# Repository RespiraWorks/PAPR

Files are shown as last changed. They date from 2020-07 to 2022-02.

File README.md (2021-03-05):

# RespiraWorks PAPR Project

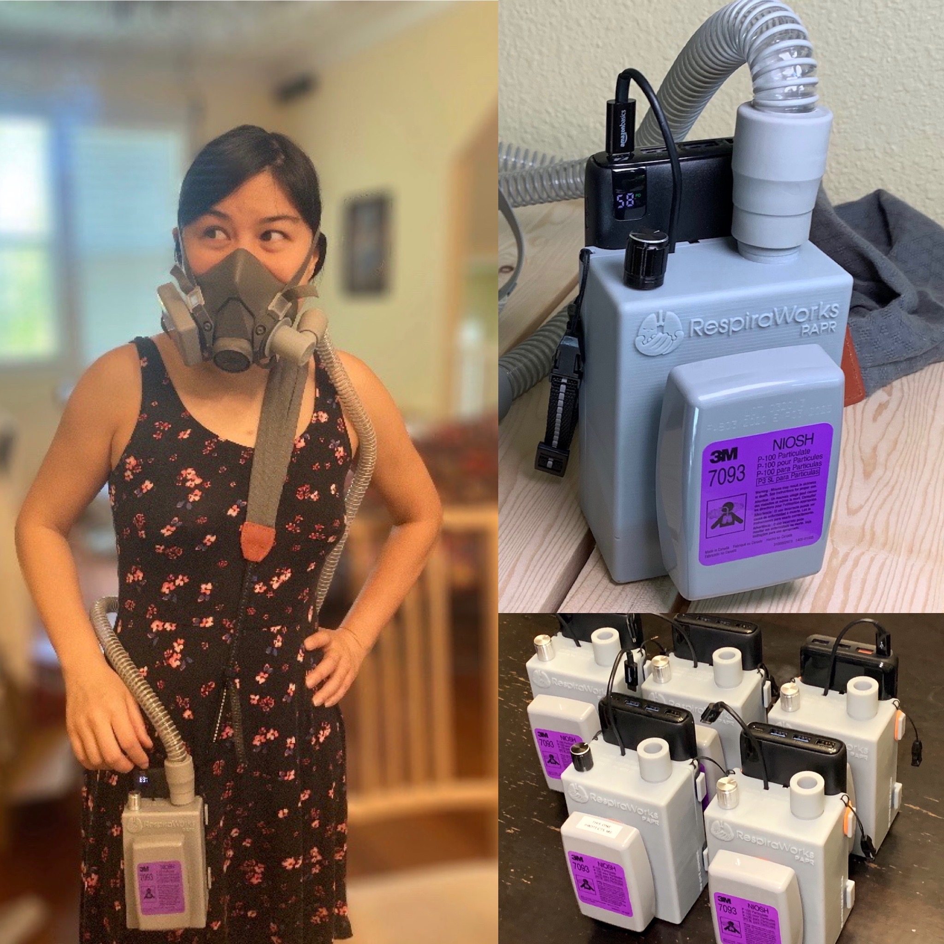
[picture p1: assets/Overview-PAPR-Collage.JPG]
Overview photo


***Important Disclaimer: This is a prototype device, offered free-of-charge as a public service during the COVID emergency, and no claim, guarantee, or warranty of performance or suitablity for any purpose is offered or implied.  This device has not been independently certified or approved.  Use of this design or any derivatives thereof is entirely at your own risk.  By using any of these materials, you acknowledge that you have read and understood the [full disclaimer](#full-disclaimer) at the end of this document.  Please do not use these materials if you do not understand and accept these risks.***

This is a low-cost 3D-printable PAPR project started by Edwin Chiu as part of RespiraWorks (github: inceptionev)

This project is currently at release-candidate stage.  The current files can be found in the release-candidates folder.  Most of the 3D files here were created in FreeCad v0.18.

The most current instructions are those in this README.  They include instructions both for building the PAPR and for modifying off-the-shelf masks, hoods, and helmets for use with the PAPR.

I am making this for myself, and for my loved ones who are medical workers and essential workers.  They wear masks all day to keep us safe, and supplies of disposable PPE are sometimes uncertain.

The combination of a respirator mask, powered air delivery, and commonly-available bayonet-mount filter packs provides a better face-seal, more comfortable breathing, and more re-usability than disposable masks. 

## Features:
- Uses commonly-available 6000-series or 7093 bayonet filter packs, which have many options in N95, P95, and P100 types.
- Powered by a USB-C PD battery pack (as long as it is 9V @ 2.0A capable)
- Packs can be swapped out for 20hrs+ of runtime per 26800mAH battery.
- If used with a modified respirator mask, it can be made to filter both inhaled and exhaled air.
- It can be used with a variety of full-head hoods, full-face masks, and respirator masks.

This project was designed in FreeCAD, and the main project file is here: [PAPRv10-MAIN.FCStd](release-candidates/PAPR-Rev10/PAPRv10-MAIN.FCStd)

Individual .stl files for 3D printing are linked in the Bill of Materials below.  Suggested support configuration and print orientation can be found in the assembly instructions below.

Also have a look at RespiraWorks' Ventilator project at https://respira.works and https://github.com/RespiraWorks/Ventilator

----

## Table of Contents
- [RespiraWorks PAPR Project](#respiraworks-papr-project)
  * [Features:](#features-)
  * [Materials](#materials)
    + [Parts to Build the PAPR](#parts-to-build-the-papr)
    + [Mask/Helmet Parts](#mask-helmet-parts)
    + [Tools and Useful Consumables](#tools-and-useful-consumables)
    + [Parts for Testing](#parts-for-testing)
  * [PAPR Assembly Instructions](#papr-assembly-instructions)
  * [Mask Assembly Instructions](#mask-assembly-instructions)
    + [6100/6200/6300 Half Facepiece Mask](#6100-6200-6300-half-facepiece-mask)
  * [Testing](#testing)
    + [To test the 6200-series masks](#to-test-the-6200-series-masks)
    + [To test the filter cartridges](#to-test-the-filter-cartridges)
  * [Future Work](#future-work)
  * [Design Diary](#design-diary)

<small><i><a href='http://ecotrust-canada.github.io/markdown-toc/'>Table of contents generated with markdown-toc</a></i></small>

----

## Materials

* **A** = Aliexpress
* **C** = McMaster-Carr
* **W** = Wonsmart
* **K** = Digikey
* **3D** = 3D printed
* **Z** = Amazon
* **R** = RS computing
* **3M** = 3M
* **G** = Grainger

### Parts to Build the PAPR

| Item | Quantity | Manufacturer  | Part #              | Price (USD)     |  Sources       | Notes |
| ---- |---------:| ------------- | ------------------- | ------------:|----------------| ----- |
| papr1   | 1 | Custom 3D print | TopLevelPart-Body | $6 (material) | [3D][3d1] | Main Body |
| papr2   | 1 | Custom 3D print | TopLevelPart-BatteryBack | $2 (material) | [3D][3d2]    | Battery Mount |
| papr3   | 1 | Custom 3D print | TopLevelPart-OutletAdapter | $1 (material) | [3D][3d3]    | 22mm Taper Hose Outlet |
| papr4   | 1 | Custom 3D print | TopLevelPart-OutletKey | $6 (material)  | [3D][3d4]    | key to hold the outlet in |
| papr5   | 1 | Wonsmart | WS7040-12-X200 | $36 | [A][1ali] | 12V Blower |
| papr6   | 1 | Generic | PotBrushlessController | $10.11 | [A][2ali] | Potentiometer-Controlled Brushless Motor Driver |
| papr7   | 1 | Generic | 9V/12V USB-C Trigger | $3.15 | [A][3ali] | USB-C 12V/9V PD Trigger - choose 9V option when ordering |
| papr8   | 1 | Amazon | 6-inch USB-C Cable | $3.50 | [Z][1azmn] | 6-inch USB-C Cable |
| papr9   | 1 | Amazon | Carry Strap | $12.59 | [Z][2amzn] | Carry Strap |
| papr10   | 1 | Littelfuse | SMAJ9.0A | $0.41 | [K][1dk] | TVS diode |
| papr11   | 1 | Various | CAP 0805 4.7uF 50V X5R | $0.27 | [K][2dk] | Filtering Cap - manufacturer stock rotates often, so search for an in-stock part |
| papr12a   | 1 | Amazon | Elastic Phone Holder | $10 | [Z][3amzn] | Elastic band to hold battery |
| papr12b   | 1 | AliExpress | Elastic Phone Holder | $0.50 | [A][5ali] | Elastic band to hold battery |
| papr13   | 1 | Conxwan | 26800mAh battery | $27 | [Z][4amzn] | 18W USB-C Battery |
| papr14   | 4 | Amazon | 6-32 x 3/8" Screws | $8.75 | [Z][5amzn] | Screws to secure back |
| papr15   | 1 | Amazon | 4ft CPAP hose | $10.57 | [Z][6amzn] | CPAP hose |
| papr16   | 1 | 3M | 7093 Filter Cartridge (pair) | $30 | [3M][3m1] | example filter packs |
| papr17   | about 6x6cm | McMaster-Carr | 8785K82-8785K822 (Extra Soft)  | $22.22/12x12" | [C][1mcmc] | 1/8" Silicone Foam Gasket Material |
| papr18   | 1 | 3M | Filter Gasket  | $2.01 | [G][1grgr] | Inlet Gasket for 6000-series filters |
| papr19   | 1 | OWO | (Optional) Upgraded potentiometer| $1.00 | [A][4ali] | nicer pot with knob and jam nut |
| papr20   | 1 | JST | (Optional) JST connector kit and crimper | $40 | [Z][8amzn] | required connectors for upgraded potentiometer |

### Mask/Helmet Parts
Parts for modifying and adapting masks and helmets for use with the PAPR

| Item | Quantity | Manufacturer  | Part #              | Price (USD)     |  Sources       | Notes |
| ---- |---------:| ------------- | ------------------- | ------------:|----------------| ----- |
| mask1   | 1 | 3M | 6100(S)/6200(M)/6300(L) Respirator Mask | $35 | [3M][3m2] | example half-face respirator mask* |
| mask2   | 1 | 3M | 6700(S)/6800(M)/6900(L) Full-Face Mask | $150 | [3M][3m3] | example full-face respirator mask* |
| mask3   | 1 | 3M | M-206 Full Face Helmet | $230 | [3M][3m4] | example full-face respiratory helmet* |
| mask4   | 1 | Allegro | Tyvek Full-Face Hood | $23 | [Z][9amzn] | example full-face hood* |
| mask5   | 1 | Custom 3D print | Bayonet Inlet Adapter | $2 (material) | [3D][3d7] | Inlet Adapter for Bayonet-type masks |
| mask6   | 1 | Custom 3D print | 6100/6200/6300 Outlet Plug | $1 (material) | [3D][3d8] | Plug for sealing the outlet valve of 6100/6200/6300 masks |
| mask7   | 1 | 3M | Inlet Filter Gasket  | $2.01 | [G][1grgr] | Inlet Gasket used as part of above outlet sealing |
| mask8   | 1 | 3D | Outlet adapter to MGHT for allegro mask | $1.00 | [3D][3d9] | Outlet adapter to allow garden hose connection |

*note, without modification, these masks do not filter the exhaled air.  They are useful for keeping the wearer safe, but not for keeping others safe from the wearer.

Some of these can be modified enable full 2-way filtering.  Instructions are planned for this lower down on this page.

### Tools and Useful Consumables
| Item | Quantity | Manufacturer  | Part #              | Price (USD)     |  Sources       | Notes |
| ---- |---------:| ------------- | ------------------- | ------------:|----------------| ----- |
| papr-tool1   | 1 | Custom 3D print | InletGasketJigInsideV1 | $1 (material) | [3D][3d5] | Jig for cutting blower inlet gasket |
| papr-tool2   | 1 | Custom 3D print | InletGasketJigOutsideV1 | $1 (material) | [3D][3d6] | Jig for cutting blower inlet gasket |
| papr-tool3   | 1 | Irwin Tools | Tap kit | $30 | [Z][10amzn] | Tap kit for chasing body threads |

**Other Useful Tools**
- Exacto blade
- 6-32 tap
- Phillips screwdriver
- Small flat-blade screwdriver (for removing outlet key)
- Assorted heat-shrink tubing or electrical tape
- Soldering iron and soldering supplies
- Small, 2mm thick needle file
- Can of compressed gas cleaner with a spray straw, like "Dust-Off" or similar, for clearing out the screw holes.

### Parts for Testing
The following adapters can be used with a Portacount machine to test the efficacy of the PAPR, masks, and the filter cartridges it uses.  Beware of counterfeit filter cartridges!  

| Item | Quantity | Manufacturer  | Part #              | Price (USD)     |  Sources       | Notes |
| ---- |---------:| ------------- | ------------------- | ------------:|----------------| ----- |
| papr-test1   | 1 | Custom 3D print | 6200SamplingAdapter | $1 (material) | [3D][3d10] | Portacount Sampling Adapter for 6200-series Masks |
| papr-test2   | 1 | Custom 3D print | BayonetFilterTester | $1 (material) | [3D][3d11] | Portacount Sampling Adapter for Bayonet-style Filter Cartridges |

[3d1]: /release-candidates/PAPR-Rev10/PAPRv10-Body.stl
[3d2]: /release-candidates/PAPR-Rev10/PAPRv10-BatteryBack.stl
[3d3]: /release-candidates/PAPR-Rev10/PAPRv10-OutletAdapter.stl
[3d4]: /release-candidates/PAPR-Rev10/PAPRv10-OutletKey.stl
[1ali]: https://www.aliexpress.com/item/32980201709.html
[2ali]: https://www.aliexpress.com/item/4001161829981.html
[3ali]: https://www.aliexpress.com/item/1005001570732005.html
[1azmn]: https://www.amazon.com/gp/product/B01LONPUM4
[2amzn]: https://www.amazon.com/gp/product/B06XDNR14N
[1dk]: https://www.digikey.com/product-detail/en/littelfuse-inc/SMAJ9.0A/SMAJ9.0ALFCT-ND/762476
[2dk]: https://www.digikey.com/product-detail/en/samsung-electro-mechanics/CL21A475KBQNNNE/1276-1248-1-ND/3889334
[3amzn]: https://www.amazon.com/gp/product/B07QTHFNYF
[4amzn]: https://www.amazon.com/gp/product/B08729Z2JX
[5amzn]: https://www.amazon.com/Stainless-Lengths-Available-Machine-Phillips/dp/B0793D86TB
[3d5]: /release-candidates/tools/InletGasketJigInsideV1.stl
[3d6]: /release-candidates/tools/InletGasketJigOutsideV1.stl
[6amzn]: https://www.amazon.com/gp/product/B01DJGLEUG
[3m1]: https://www.3m.com/3M/en_US/company-us/all-3m-products/~/3M-Particulate-Filter-7093-P100-60-EA-Case/?N=5002385+3294776429&rt=rud
[3m2]: https://www.3m.com/3M/en_US/company-us/all-3m-products/~/All-3M-Products/Personal-Protective-Equipment/Reusable-Respirators/Half-Facepiece-Respirators/3M-Half-Facepiece-Reusable-Respirators-6000-Series/?N=5002385+8711017+8720539+8720550+8720785+8726639+3294857497&rt=r3
[7amzn]: https://www.amazon.com/gp/product/B07BKP6KFX
[4ali]: https://www.aliexpress.com/item/10000192070172.html
[8amzn]: https://www.amazon.com/gp/product/B07R1H3Z8X
[1mcmc]: https://www.mcmaster.com/8785K82-8785K822/
[3m3]: https://www.3m.com/3M/en_US/company-us/all-3m-products/~/All-3M-Products/Personal-Protective-Equipment/Reusable-Respirators/Full-Facepiece-Respirators/3M-Full-Facepiece-Reusable-Respirators-6000-Series/?N=5002385+8711017+8720539+8720550+8720784+8726633+3294857497&rt=r3
[3m4]: https://www.3m.com/3M/en_US/company-us/all-3m-products/~/3M-Versaflo-Respiratory-Faceshield-Assembly-M-206-37299-AAD-with-Comfort-Faceseal-1-EA-Case/?N=5002385+3292194464&preselect=3293786499&rt=rud
[9amzn]: https://www.amazon.com/gp/product/B012D8N4I6/
[1grgr]: https://www.grainger.com/product/3M-Inhalation-Port-Gasket-3PRG7
[3d7]: /release-candidates/PAPRmasks/PAPRmasks-BayonetInletAdapter-V1.stl
[3d8]: /release-candidates/PAPRmasks/PAPRmasks-6200-OutletPlug-V1.stl
[3d9]: /sandbox/PAPR-OutletAdapter-V9-with_MGHT.STL
[3d10]: /release-candidates/PAPRtest/PAPRtest-Portacount-6200SamplingAdapter.stl
[3d11]: /release-candidates/PAPRtest/PAPRtest-Portacount-BayonetFilterTester.stl
[10amzn]: https://www.amazon.com/Tools-Machine-Fractional-12-Piece-24605/dp/B00004YOAZ
[5ali]: https://www.aliexpress.com/item/4000278505876.html

## Useful Media
| Graphic for printing Outlet Stickers | Info cards (useful on planes or for the curious) Click image for PDF |
|:--------------------------:|:---------------------------:|
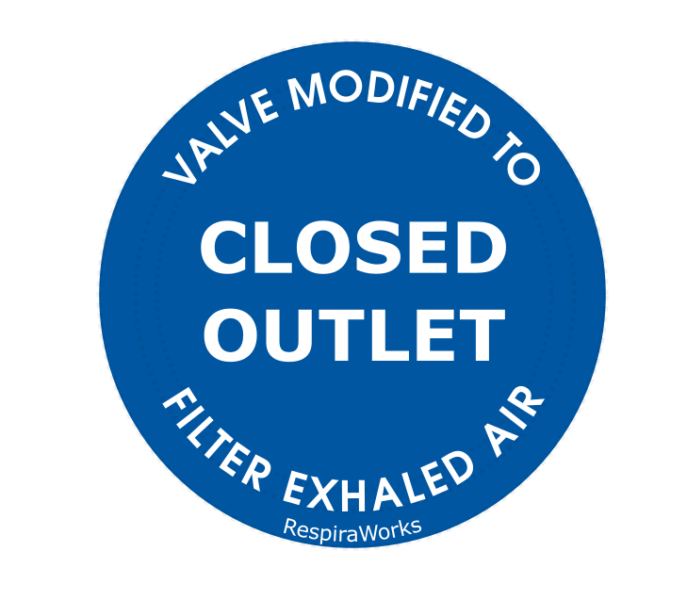
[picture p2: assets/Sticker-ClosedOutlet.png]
Outlet Stickers
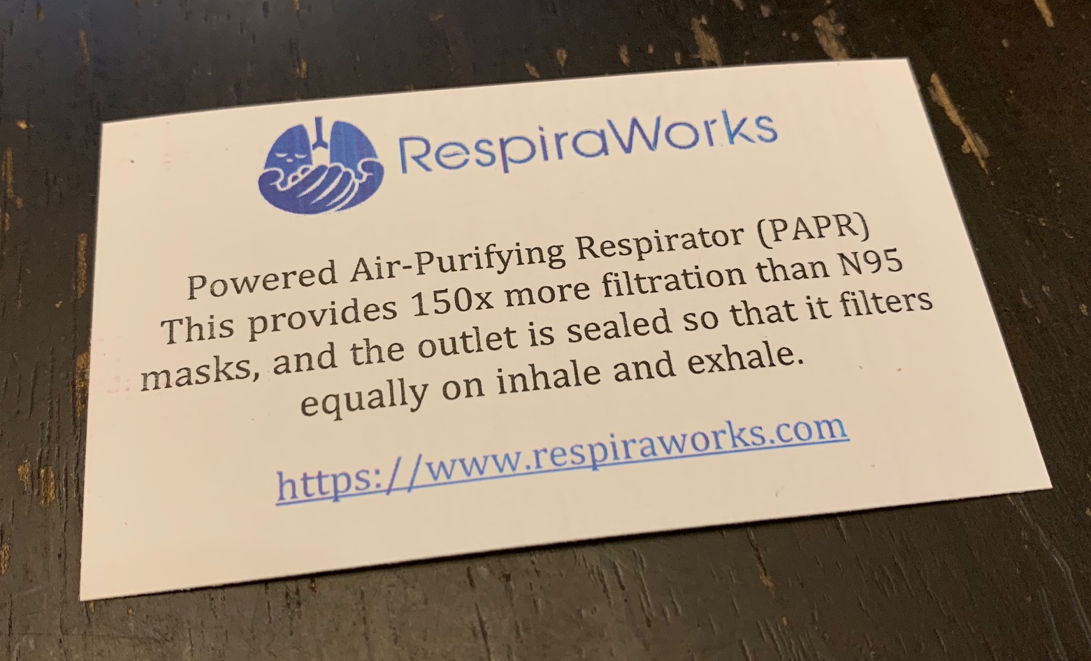
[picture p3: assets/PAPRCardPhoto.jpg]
|  |  | 

----

## PAPR Assembly Instructions

**Step 1:** Print out all the 3D printed parts and tools.  Tip: Select the print orientation such that supports fall on flat/inside faces, and avoid supports on text.  Note that depending on your printer, you may need to chase the screw threads with a 6-32 tap.

The PAPR was designed and tested using the following setup.  You may need to make modifications for your printer/material/setup.
- Printer: Elegoo Mars (SLA LCD Masking 3D Printer)
- Material: Blend of 30% Siraya Tech Tenacious and 70% Siraya Tech Fast Grey
 - This blend makes a material that is strong but also slightly flexible and thus resistant to cracking due to impacts.
- Layer Thickness: 0.05mm
- Exposure time (bottom layers): 30s
- Expposure time (all other layers): 8s

**Suggested Print Orientations**

**Body**
- Tilt angle: 4.0° lean back
- This allows the supports to come in at an angle that makes them easier to remove.
- This is the maximum angle that still allows the supports needed to correctly print the bayonet teeth in the inlet.
- This orientation preserves the quality of the printed text.
- Most printing processes will require that the 6-32 threads the body be chased with a 6-32 tap.  I recommend doing this step before post-curing, while the resin is still soft.
- Whether you chase the threads before or after post-curing, you MUST clear any uncured resin out of the thread holes before post-curing.  If the residual resin cures inside the holes, it will plug the threads.  A can of compressed gas keyboard cleaner that comes with a straw for directing the flow can be very useful here.
- Having a 2mm thick needle file can be useful for clearing residue from the supports in the outlet adapter key slot.
- This Chitubox project file reflects the recommended supports and orientation: [_PAPRv10-Body.chitubox](release-candidates/PAPR-Rev10/_PAPRv10-Body.chitubox)

|                            |                             |
|:--------------------------:|:---------------------------:|
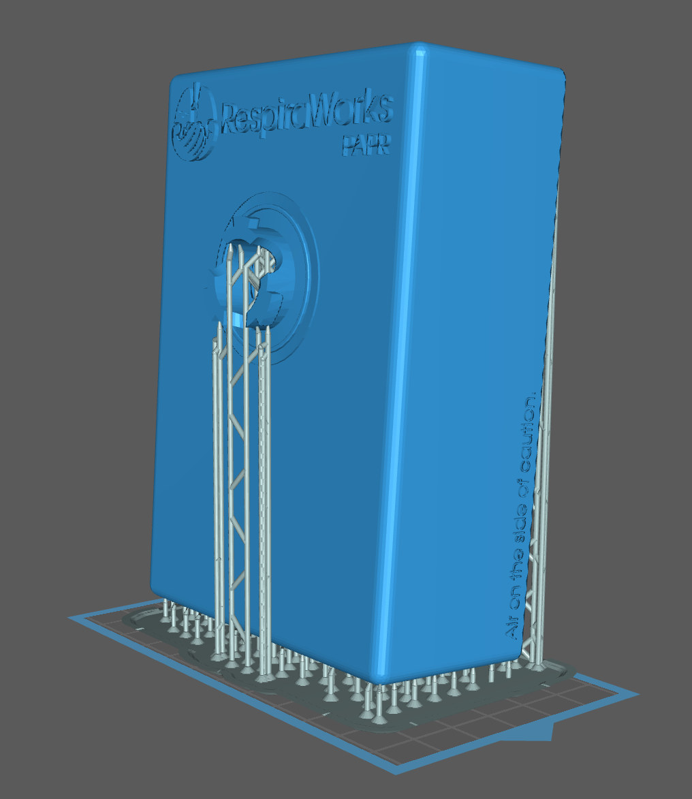
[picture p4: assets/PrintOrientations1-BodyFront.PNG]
Print Orientation: Body Front
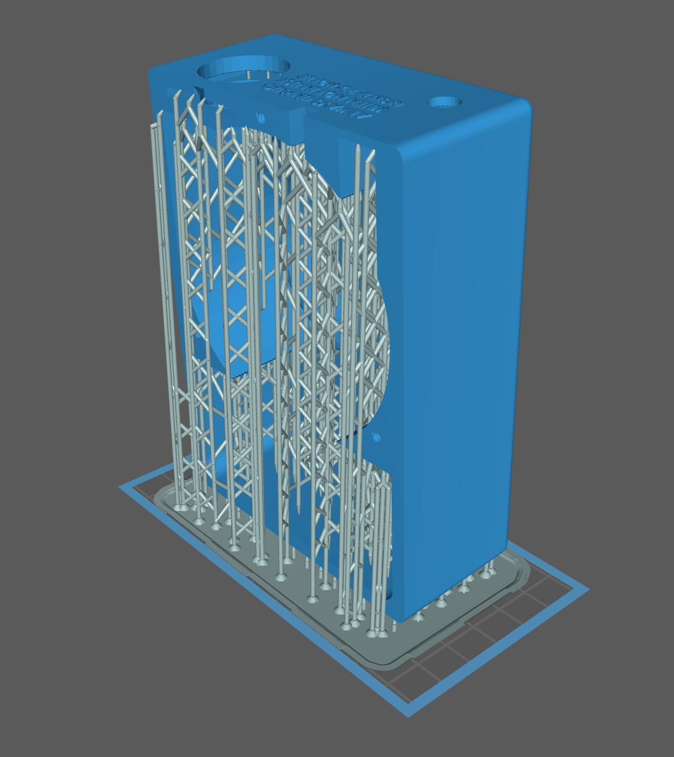
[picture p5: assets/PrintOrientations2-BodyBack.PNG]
Print Orientation: Body Back
|  |  |

**Battery Back**
- Tilt angle: 11° lean back
- These minimal supports were confirmed to print reliably with the settings above.
- This orientation keeps the inside surface of the back flat, which is required for pushing the blower into the gasket.
- This Chitubox project file reflects the recommended supports and orientation: [_PAPRv10-BatteryBack.chitubox](release-candidates/PAPR-Rev10/_PAPRv10-BatteryBack.chitubox)

|                            |                             |
|:--------------------------:|:---------------------------:|
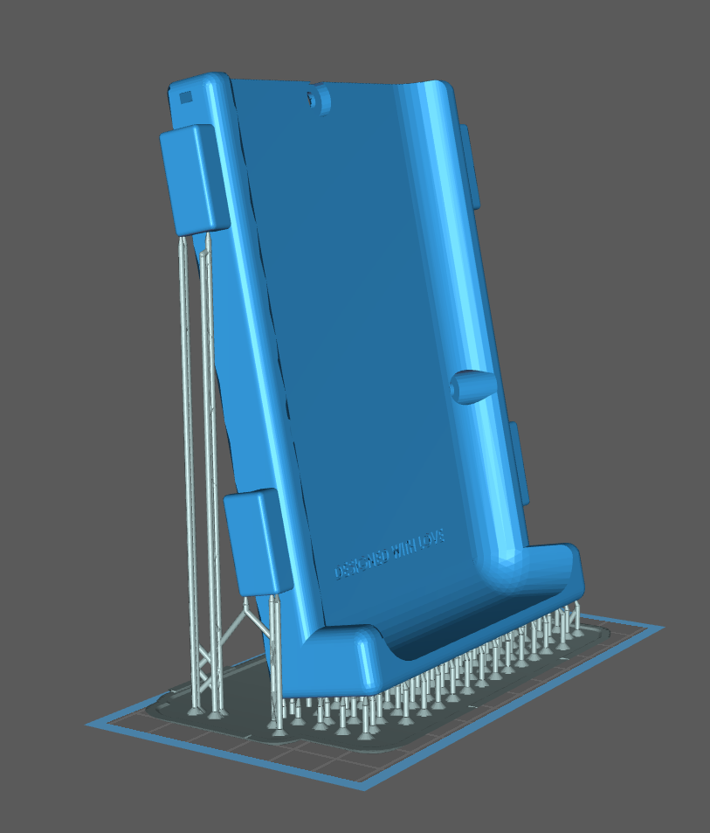
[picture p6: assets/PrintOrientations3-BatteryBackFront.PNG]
Print Orientation: Battery Back Front
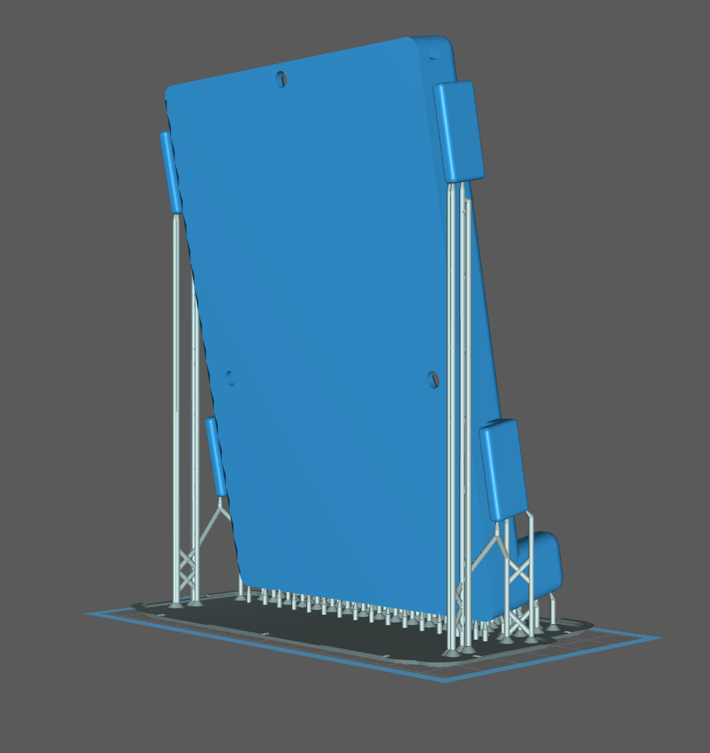
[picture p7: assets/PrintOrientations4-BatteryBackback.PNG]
Print Orientation: Body Back Back
|  |  |

**Small Parts**
- Only the outlet adapter and outlet key are required to build the PAPR, but if you are making the 6100/6200/6300 mask mods, you can combine the inlet adapter and outlet plug on this print.
- Tilt angle: 4° on the mask inlet adapter only.  This overhangs the front face, allowing supports to reach the engagement teeth.
- These supports on the mask inlet adapter are necessary to make those teeth print correctly.
- Supports are necessary on the outlet adapter as well, to prevent vacuum formation, which can distort or fail the print.
- Supports are not technically necessary on the outlet plug and outlet key, but the rafts make removal from the build plate easier, and prevent bottom layer over-exposure distortions which you would otherwise need to remove during post-processing.
- This Chitubox project file reflects the recommended supports and orientation: [_PAPRv10-SmallParts.chitubox](release-candidates/PAPR-Rev10/_PAPRv10-SmallParts.chitubox)

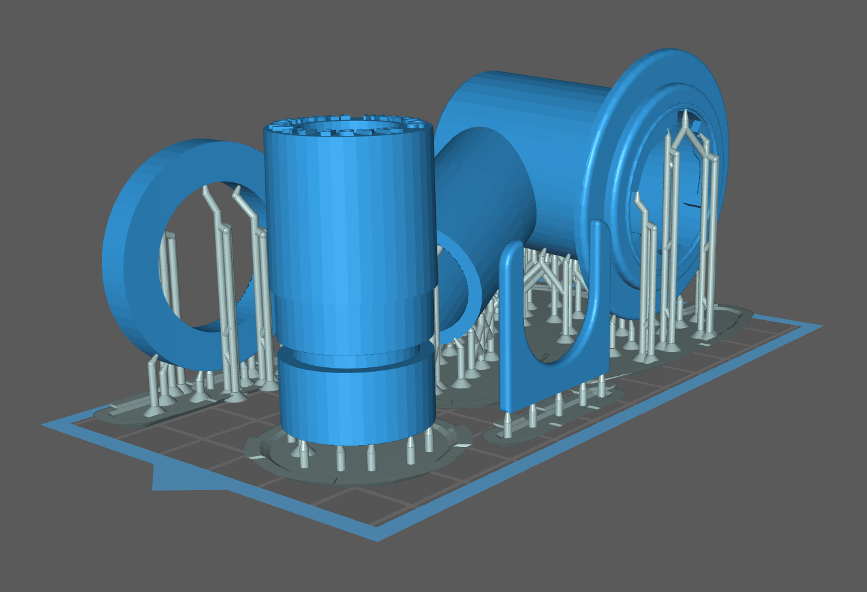
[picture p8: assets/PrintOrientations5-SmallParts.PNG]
Print Orientation: Small Parts


**Other Printing Tips:**

- Good curing is key.  I recommend 60min under 405nm 6W lights minimum.  Turn your parts to make sure no portions stay shadowed during curing.
- Keep the alcohol wash short, 5min maximum.  Parts left in alcohol for too long will swell and lose strength.
- The next build steps can be done while the parts are being printed.  
- The first part you will need in the following assembly process is the Gasket Jigs so if you print those first you can get moving.  The next part is the body, followed by the outlet adapter and the outlet adapter key, and finally, the battery back. 

**Step 2:** Gather your electrical parts.

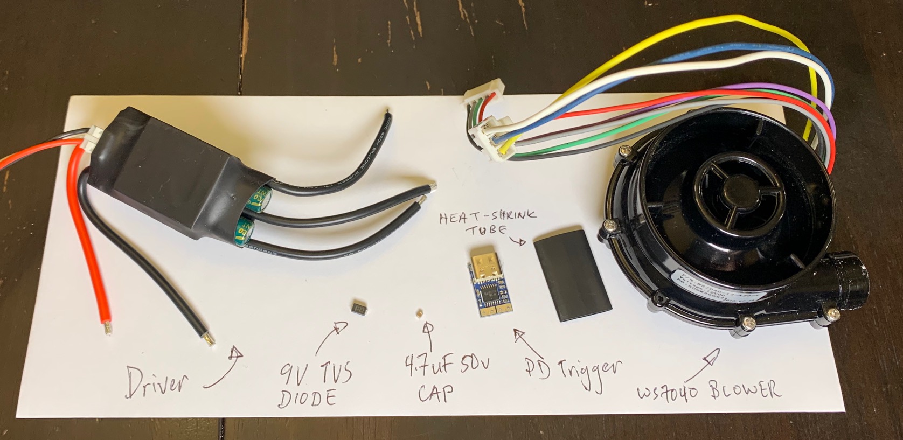
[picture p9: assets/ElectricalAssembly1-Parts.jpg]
Electrical Parts


**Step 3:** Prepare the PD Trigger.  Here will we set the voltage to 9V and add voltage protection to the output.  

Removing the solder bridge sets the PD mode to 9V.

The diode and cap are necessary to protect the battery from receiving damaging voltage kickback from the motor driver.  

|                            |                             |
|:--------------------------:|:---------------------------:|
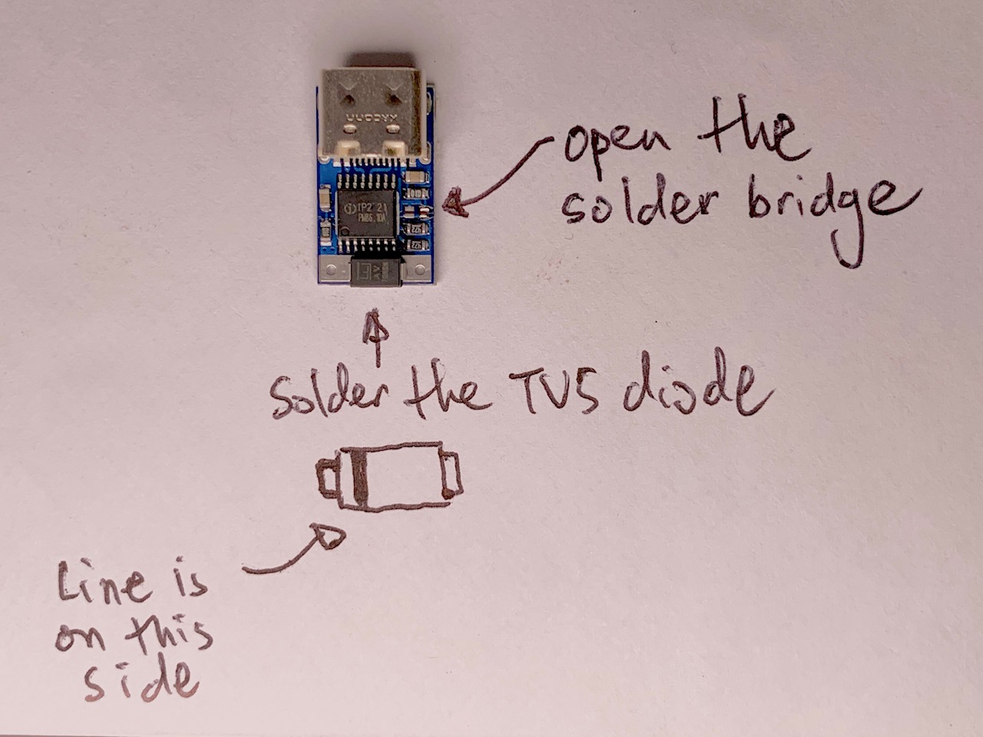
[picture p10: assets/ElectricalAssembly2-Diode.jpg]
Trigger Voltage and Diode
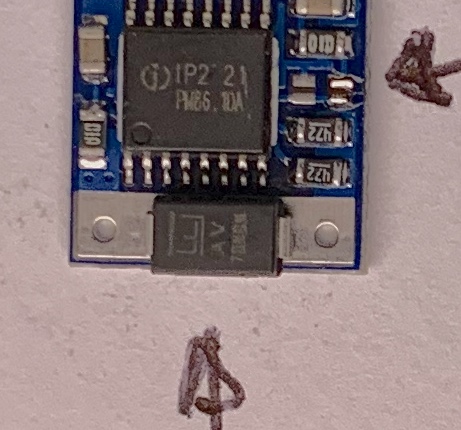
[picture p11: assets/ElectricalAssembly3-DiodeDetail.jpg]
Diode Detail
|  |  |

The diode has a line indicating the cathode.  Make sure the side with the line goes to positive (+) on the trigger.  

Now flip the PD Trigger over and solder the 4.7uF 50V cap to the backside between the two metal thru-holes.

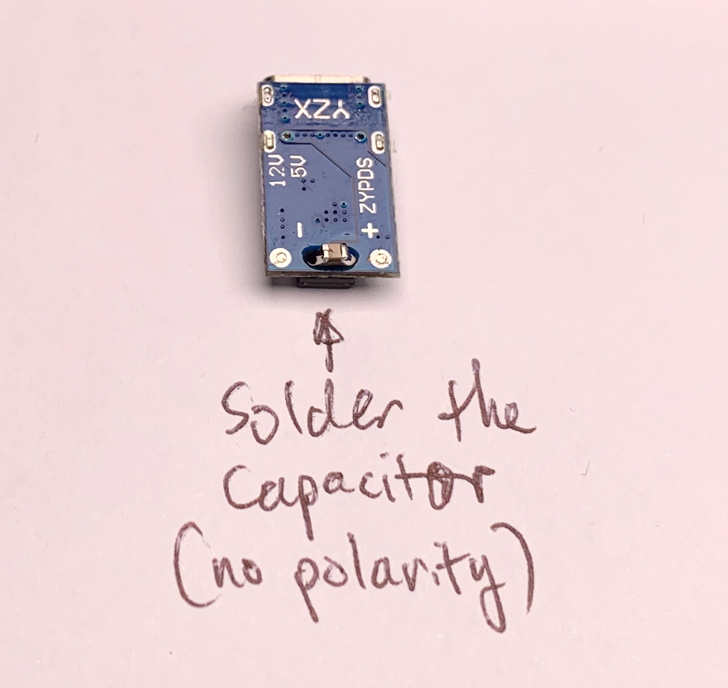
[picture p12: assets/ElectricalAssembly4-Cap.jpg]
Cap


Then solder the motor controller wires to the pads on the trigger.  Heat shrink anound the completed trigger assembly.

|                            |                             |
|:--------------------------:|:---------------------------:|
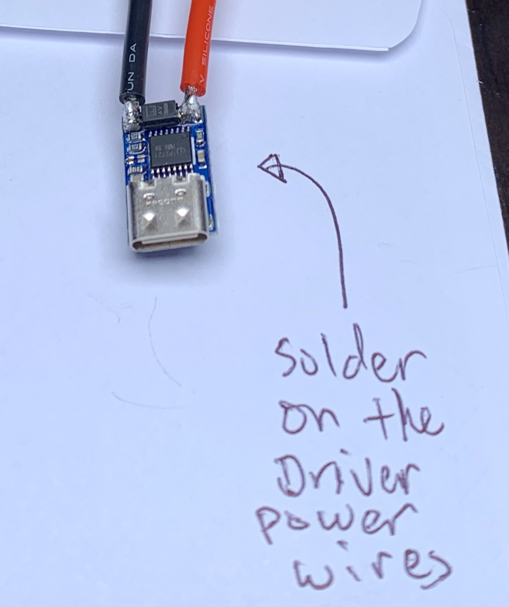
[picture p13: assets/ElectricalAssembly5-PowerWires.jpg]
Power Wires
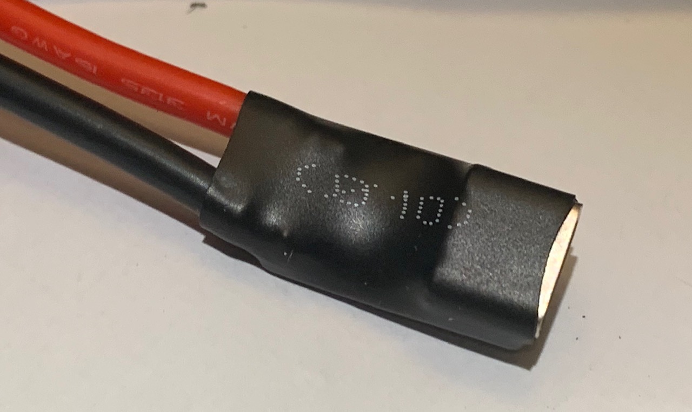
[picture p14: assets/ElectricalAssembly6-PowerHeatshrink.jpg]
PD Trigger Heat Shrink
|  |  |

**Step 4:** Attach the driver to the blower.  Make sure to observe the right pin assignments as pictured or the blower will spin backwards.

Cut the White, Yellow, and Blue blower wires near the connector, preserving as much length as possible.  Cut some heat shrink tubing and put them on the blower wires before you proceed.

Trim the driver's black phase wires short and strip them as pictured.  Solder the blower and driver phase wires as pictured, being mindful of the driver orientation (capacitors below wires).  Apply the heat shrink tubing.

|                            |                             |
|:--------------------------:|:---------------------------:|
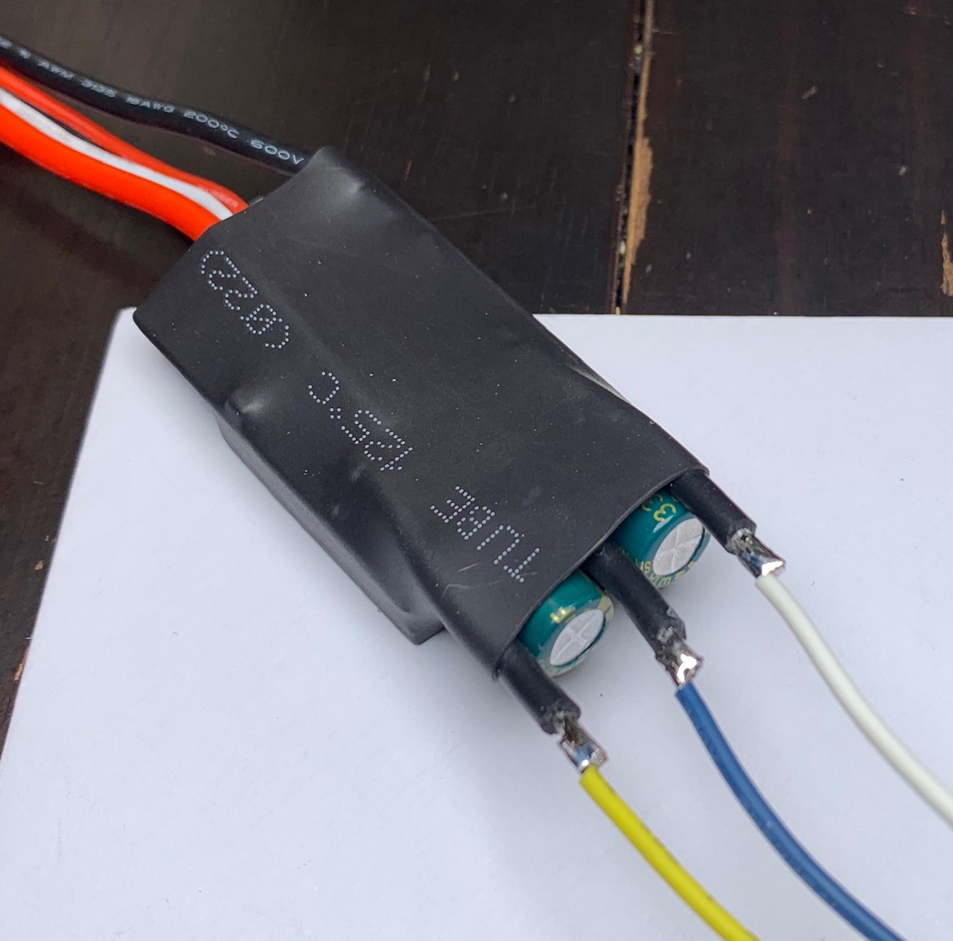
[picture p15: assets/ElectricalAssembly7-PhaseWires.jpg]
Phase Wires
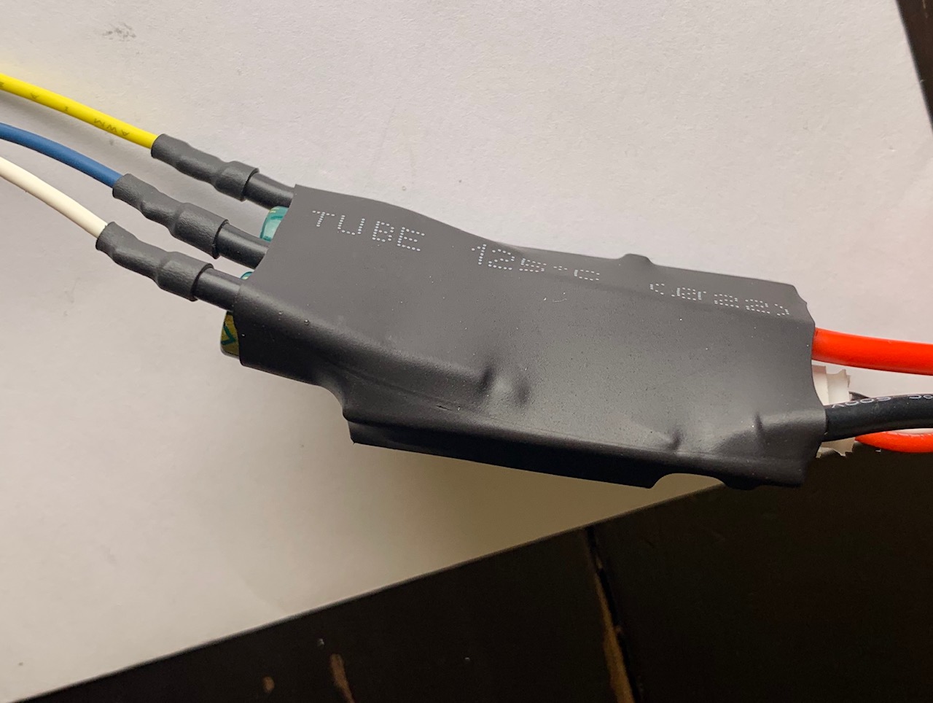
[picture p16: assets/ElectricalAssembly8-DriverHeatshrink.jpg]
Phase Wires Heat Shrink
|  |  |

**Step 5:** Install the pot into the body.  If you are using the included pot that comes with the driver, most of these steps will be optional.  For the included pot, push the pot into the slot and through the shaft hole, and glue it in place with some hot glue.  If you are using the upgraded pot with knob, follow these instructions:

Take the included pot and cut off the wires, preserving the connector and wires.

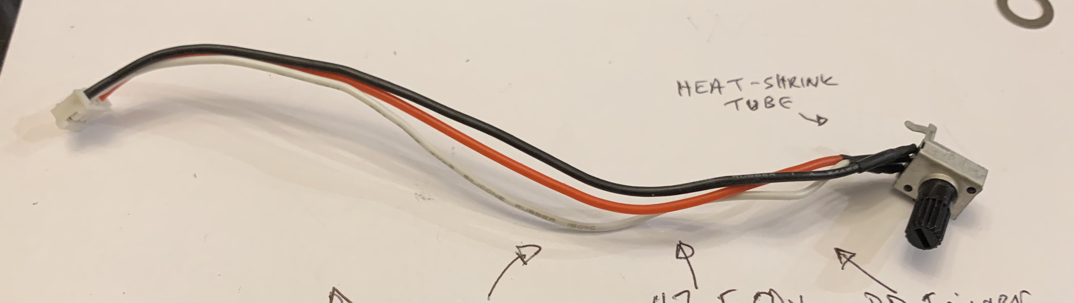
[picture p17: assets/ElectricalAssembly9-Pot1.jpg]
Included pot


Crimp JST XH sockets onto the ends of these pins.  Populate the sockets into a 3-pin female JST XH housing, using the old pot as a guide for the pin arrangement.  Insert the connector into the pot PCB.

|                            |                             |
|:--------------------------:|:---------------------------:|
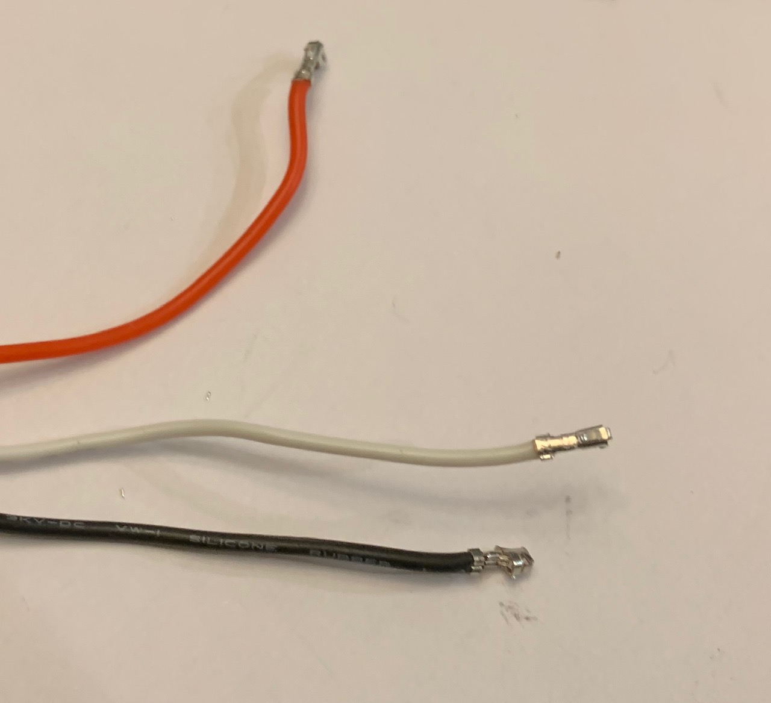
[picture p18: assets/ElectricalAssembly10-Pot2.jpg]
Pot Wire Crimps
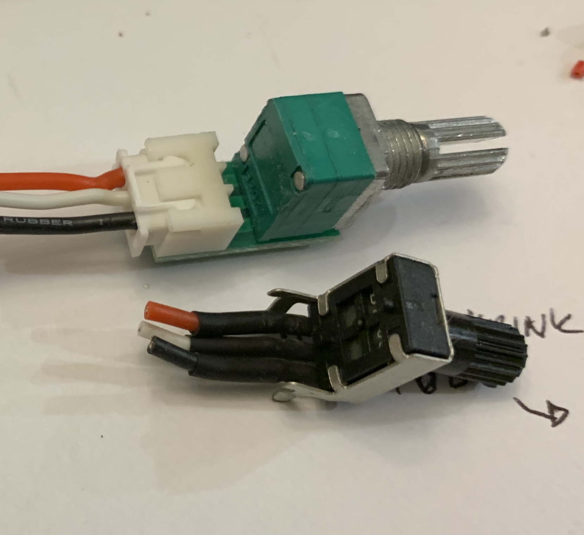
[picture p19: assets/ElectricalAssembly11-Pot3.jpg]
Pot Wire Connector
|  |  |

Remove the knob, nut, and washer from the pot.  The knob is push-fit and just slides off.  Install it into the slot and through the shaft hole with the PCB up against the inner wall.  Route the wires through the groove.  

|                            |                             |
|:--------------------------:|:---------------------------:|
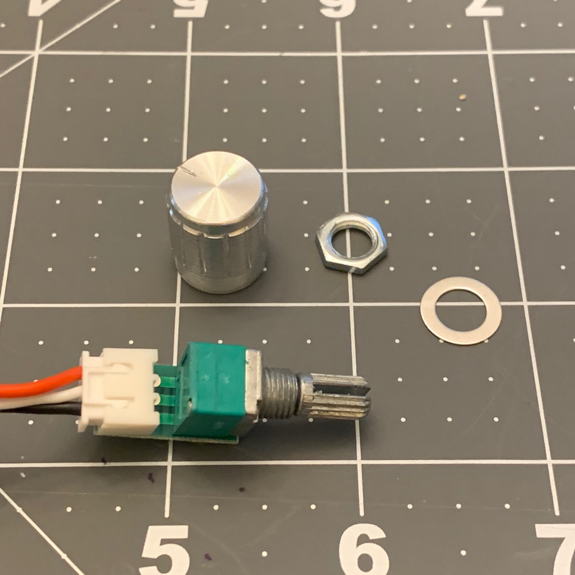
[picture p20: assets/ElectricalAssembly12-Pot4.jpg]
Pot hardware
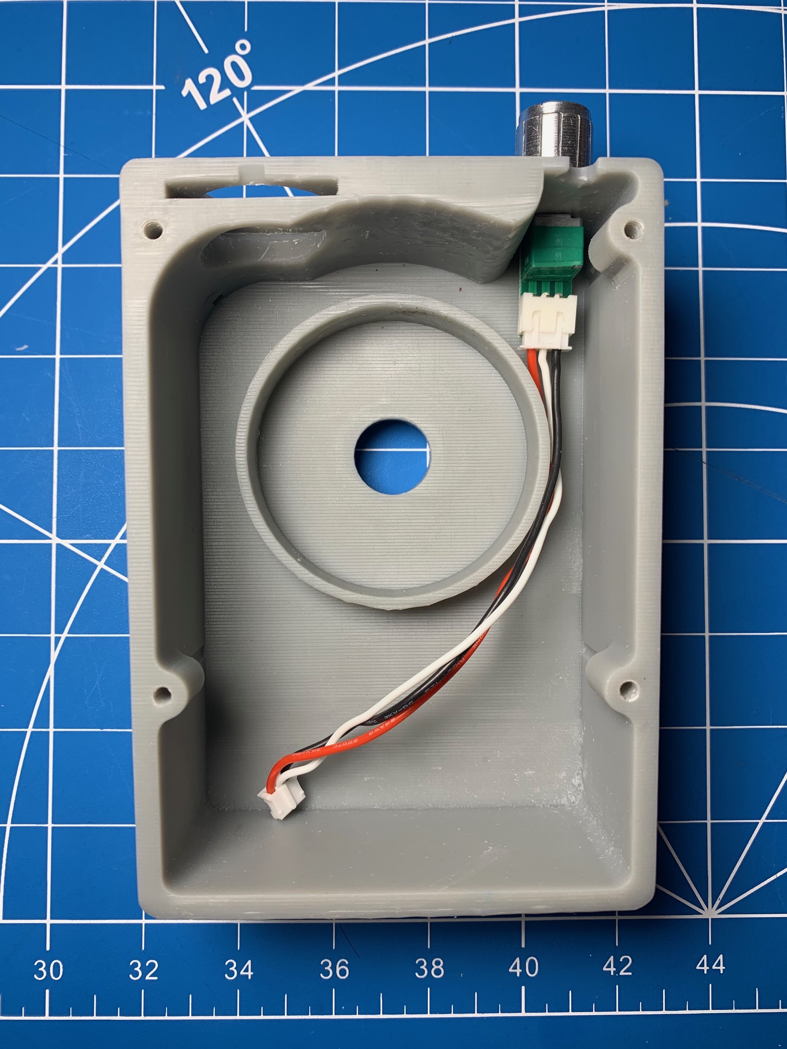
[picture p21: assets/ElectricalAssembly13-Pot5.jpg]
Pot placement
|  |  |

From the other side, install the washer and nut and tighten to retain the pot.  Install the push-fit knob.

|                            |                             |
|:--------------------------:|:---------------------------:|
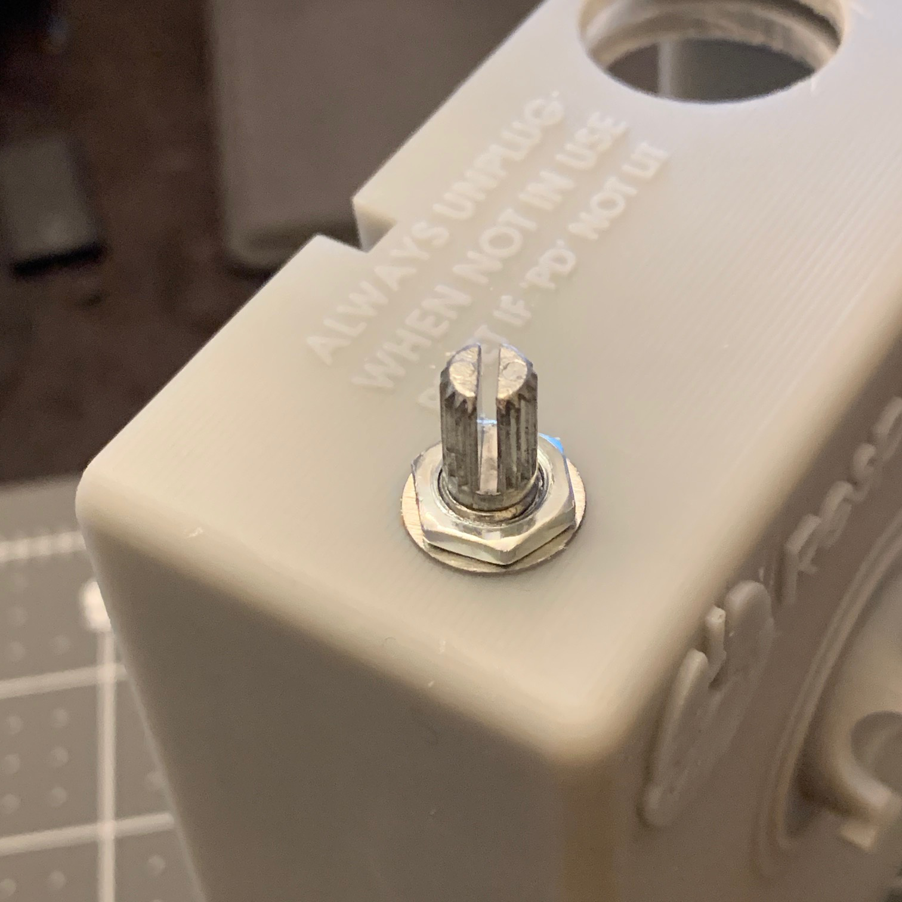
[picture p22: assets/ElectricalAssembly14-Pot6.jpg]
Pot Installation
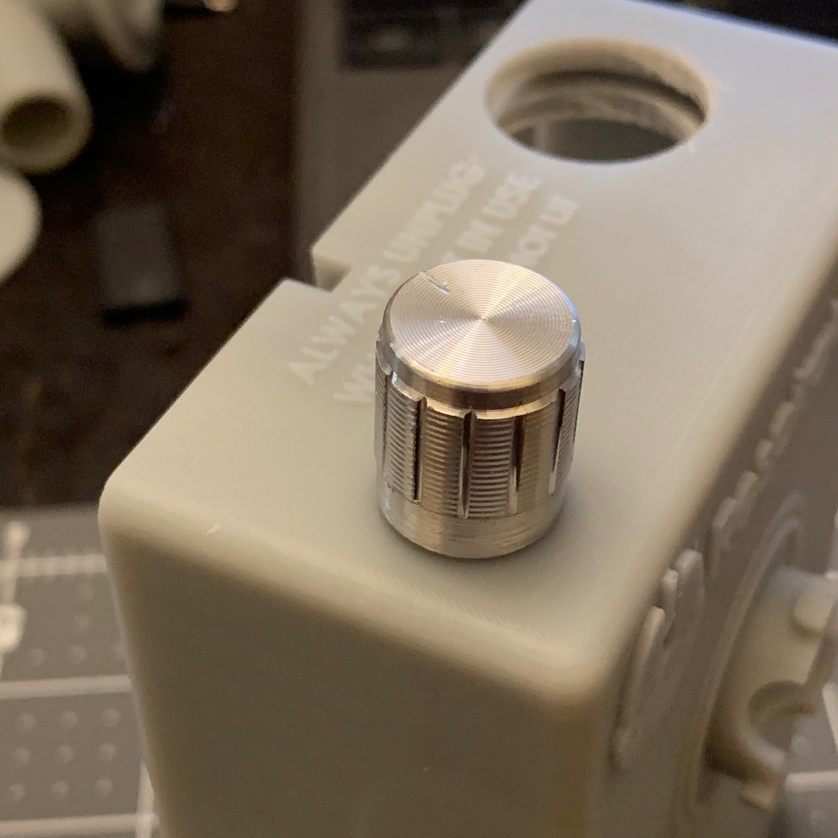
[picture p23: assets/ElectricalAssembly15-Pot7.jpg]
Knob Installtion
|  |  |

Plug the other end of the pot wires into the driver.

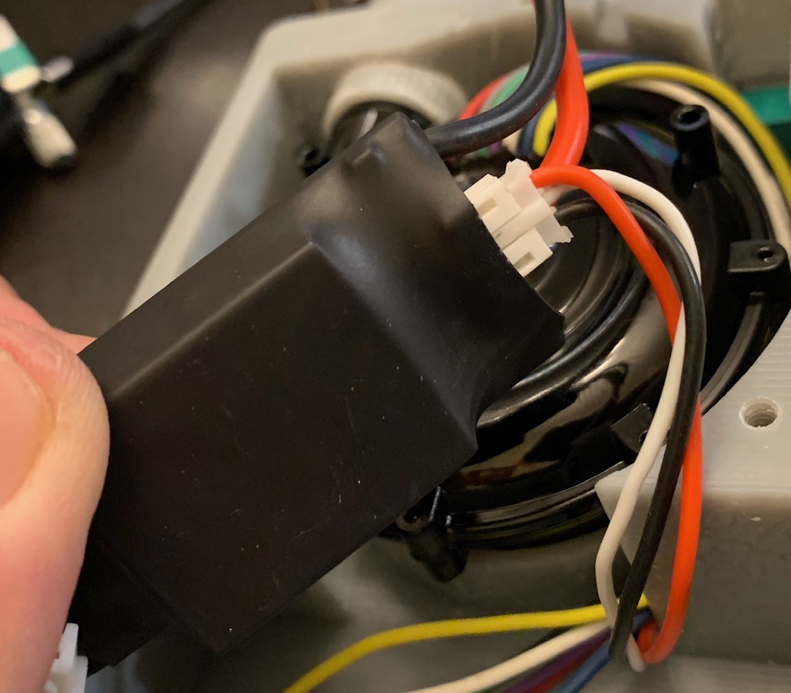
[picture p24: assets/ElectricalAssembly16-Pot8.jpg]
Driver Pot Connection


**Step 6:** Use the gasket jigs to cut out the blower inlet gasket from the gasket material.

First, make sure you have enough room to cut out the blower inlet gasket. Place the inner gasket jig and use it to make the inner cut.

|                            |                             |
|:--------------------------:|:---------------------------:|
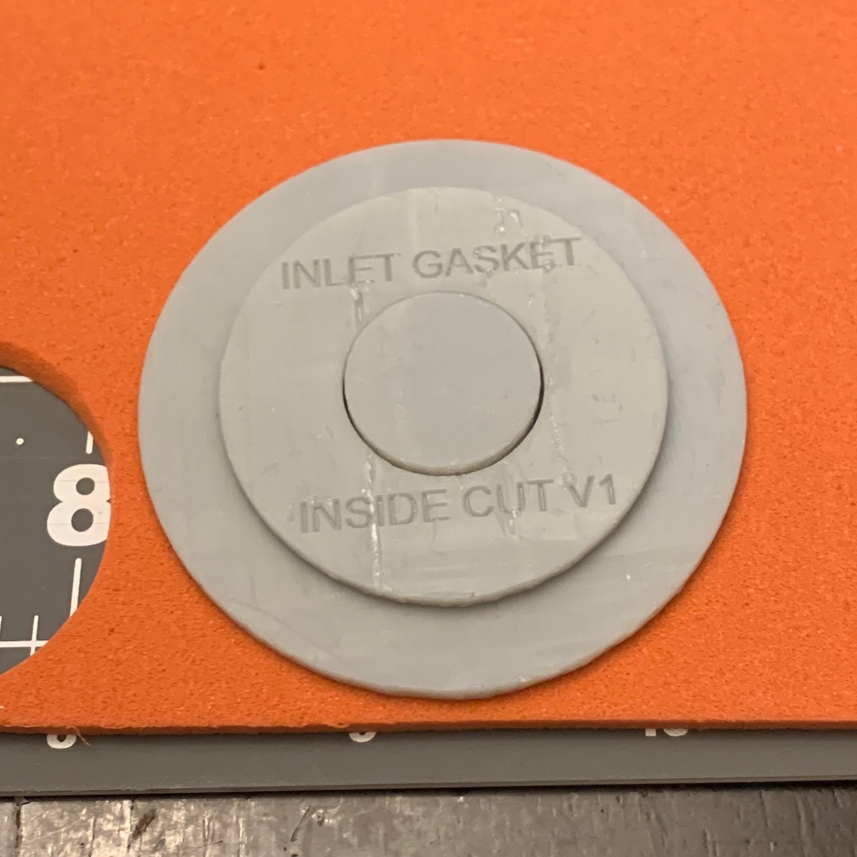
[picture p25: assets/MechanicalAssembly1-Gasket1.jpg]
Gasket Material
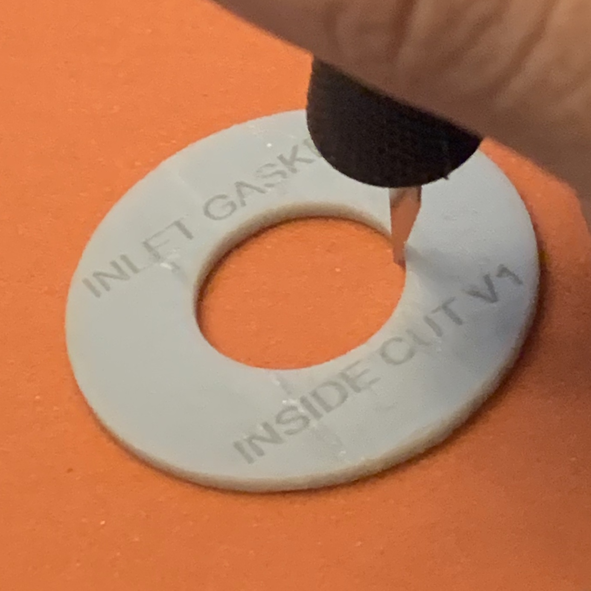
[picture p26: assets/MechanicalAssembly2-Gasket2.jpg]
Gasket inner cut
|  |  |

Place the outer gasket jig into the hole you just cut and use it to make the outer cut.

|                            |                             |
|:--------------------------:|:---------------------------:|
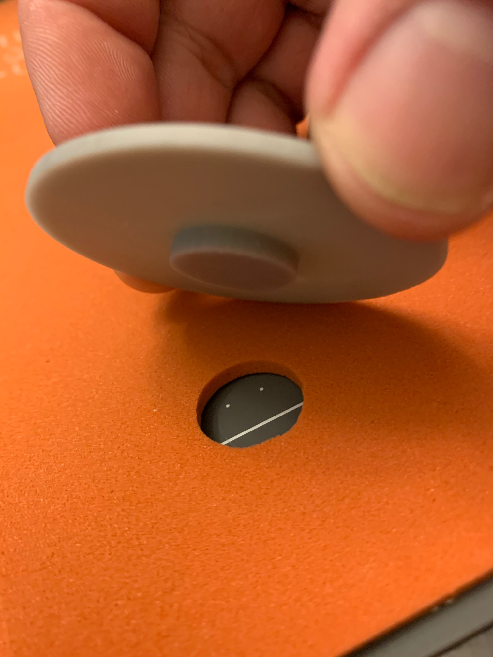
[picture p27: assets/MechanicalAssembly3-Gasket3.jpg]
Outer Gasket Jig
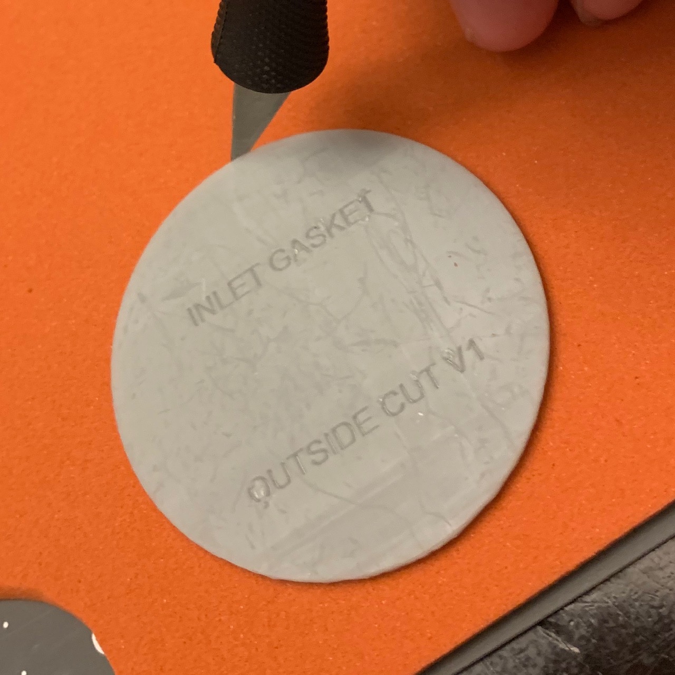
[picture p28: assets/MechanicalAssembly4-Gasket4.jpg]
Gasket outer cut
|  |  |

Insert the completed blower inlet gasket into the housing.

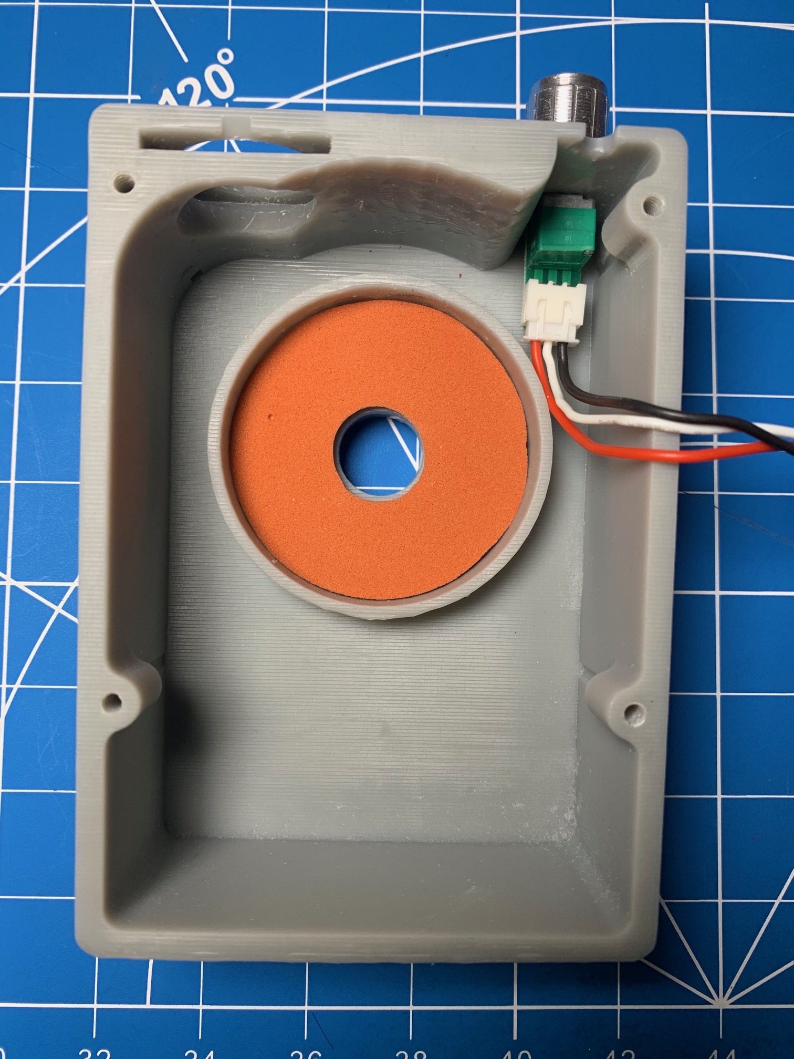
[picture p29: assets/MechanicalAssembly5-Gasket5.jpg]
Inlet Gasket Placement


**Step 7:** Install the blower into the housing.

Put the blower into the pocket over the gasket.

|                            |                             |
|:--------------------------:|:---------------------------:|
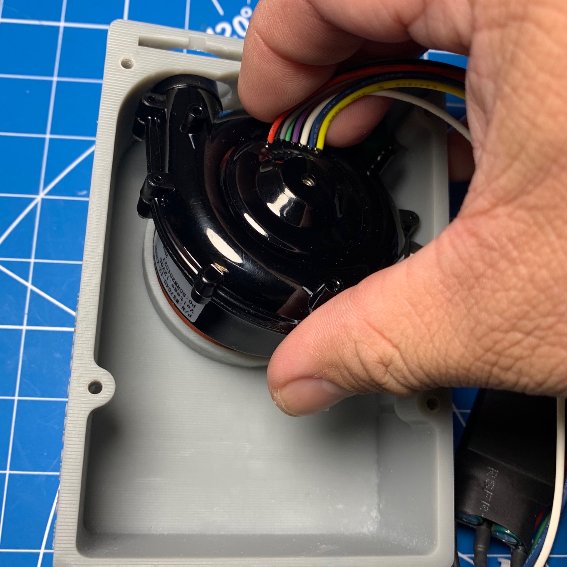
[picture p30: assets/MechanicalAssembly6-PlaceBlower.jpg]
Place the Blower
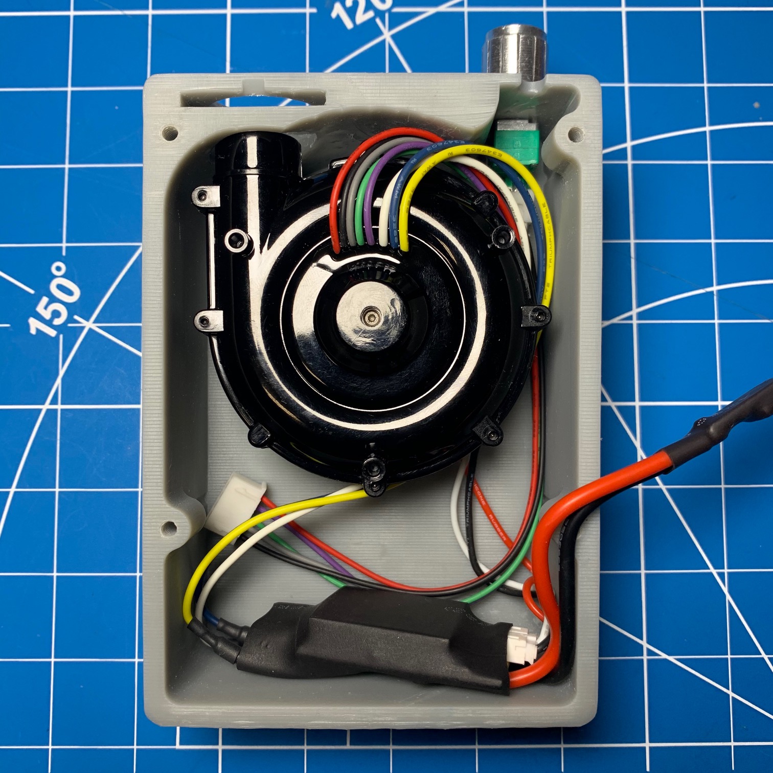
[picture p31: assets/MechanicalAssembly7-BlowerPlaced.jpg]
Place the Blower
|  |  |

Insert the outlet adapter through the hole at the top of the housing and install the retaining key.

|                            |                             |                             |
|:--------------------------:|:---------------------------:|:---------------------------:|
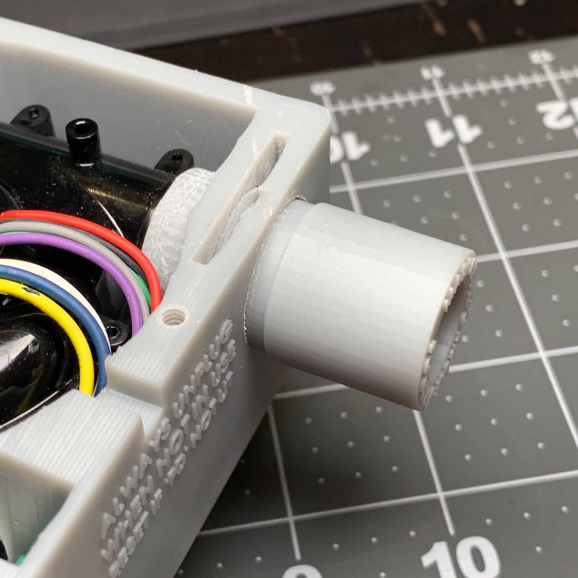
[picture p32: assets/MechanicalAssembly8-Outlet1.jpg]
Outlet Adapter Placement
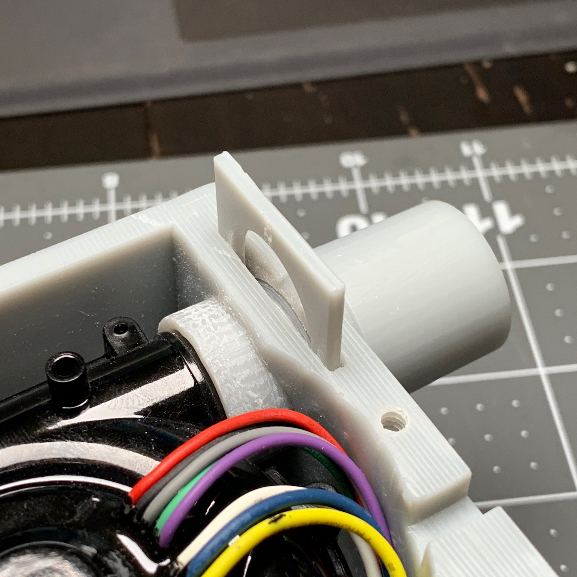
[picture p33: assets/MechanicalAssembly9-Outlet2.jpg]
Outlet Key Placement
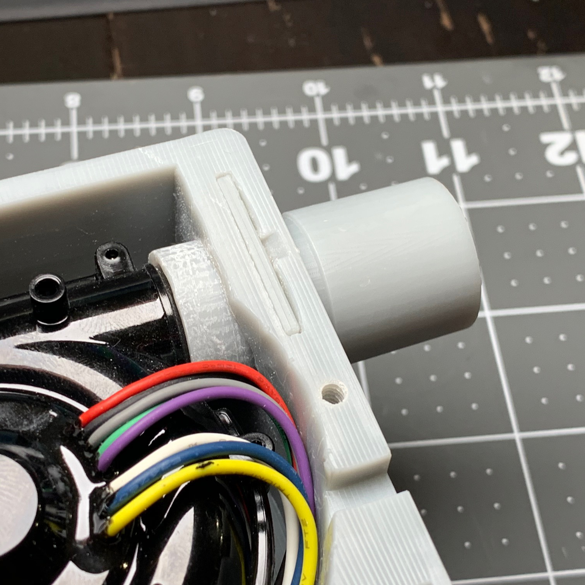
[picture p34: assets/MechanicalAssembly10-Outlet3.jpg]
Outlet Complete
|  |  | 

Route the wires back through the groove to the electronics pocket.  Fit the driver and PD trigger into this pocket.  Install the 6" USB-C cable into the PD trigger and route it as shown, along the right side under the blower and out the top of the housing.

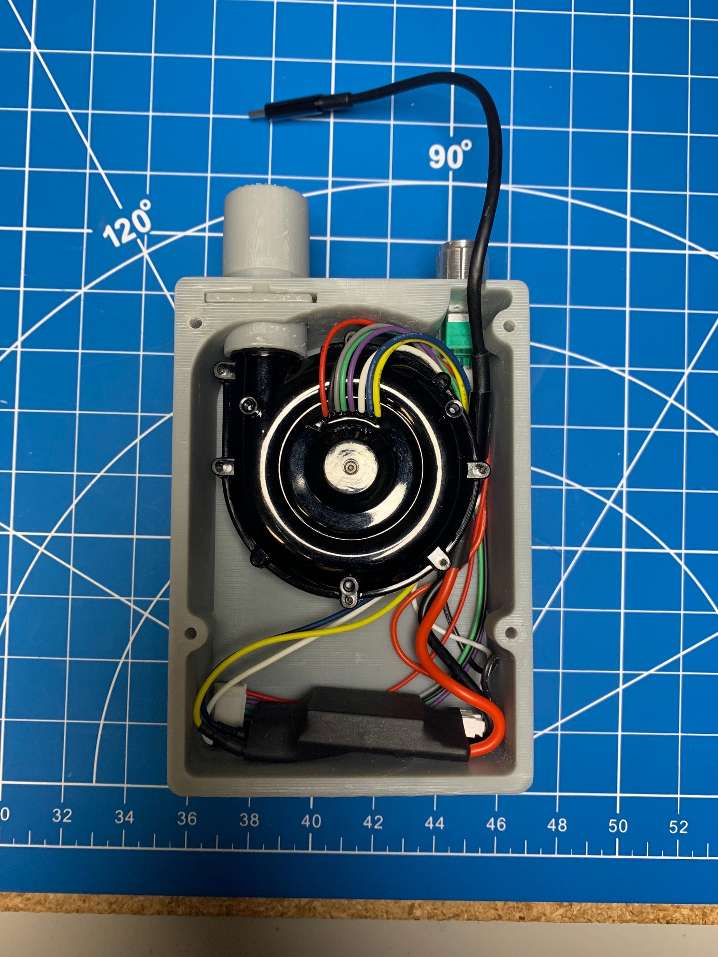
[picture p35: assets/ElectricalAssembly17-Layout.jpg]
Electronics Layout


If for some reason you ever need to remove the outlet adapter key, wedge a screwdriver into the provided notch and lever it out.

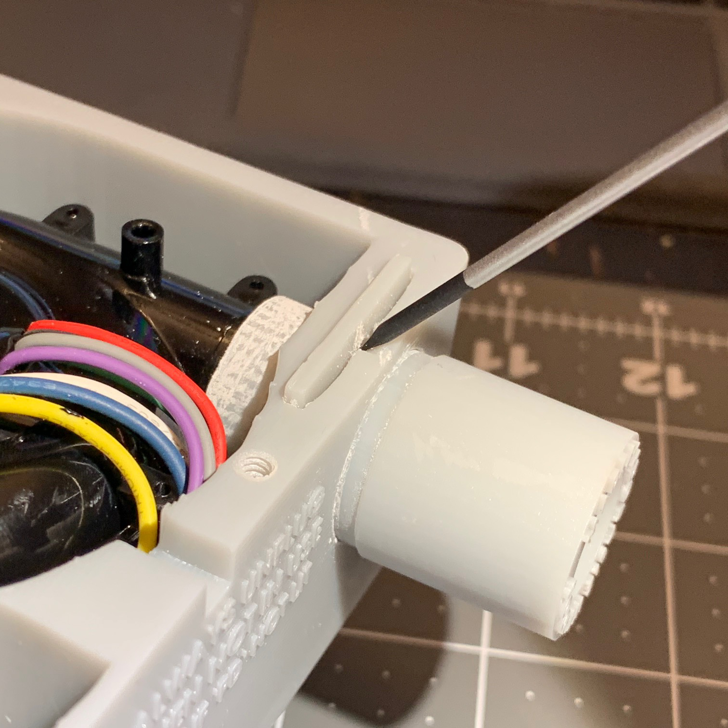
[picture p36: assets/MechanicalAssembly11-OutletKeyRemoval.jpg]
Outlet Key Removal


**Step 8:** Install the battery back, being careful not to pinch any wires.  It may help to slide it on, while holding the wires in place. Use the screws to secure the battery back onto the body. Install the battery into the PAPR and secure it with the elastic cage.

|                            |                             |                             |
|:--------------------------:|:---------------------------:|:---------------------------:|
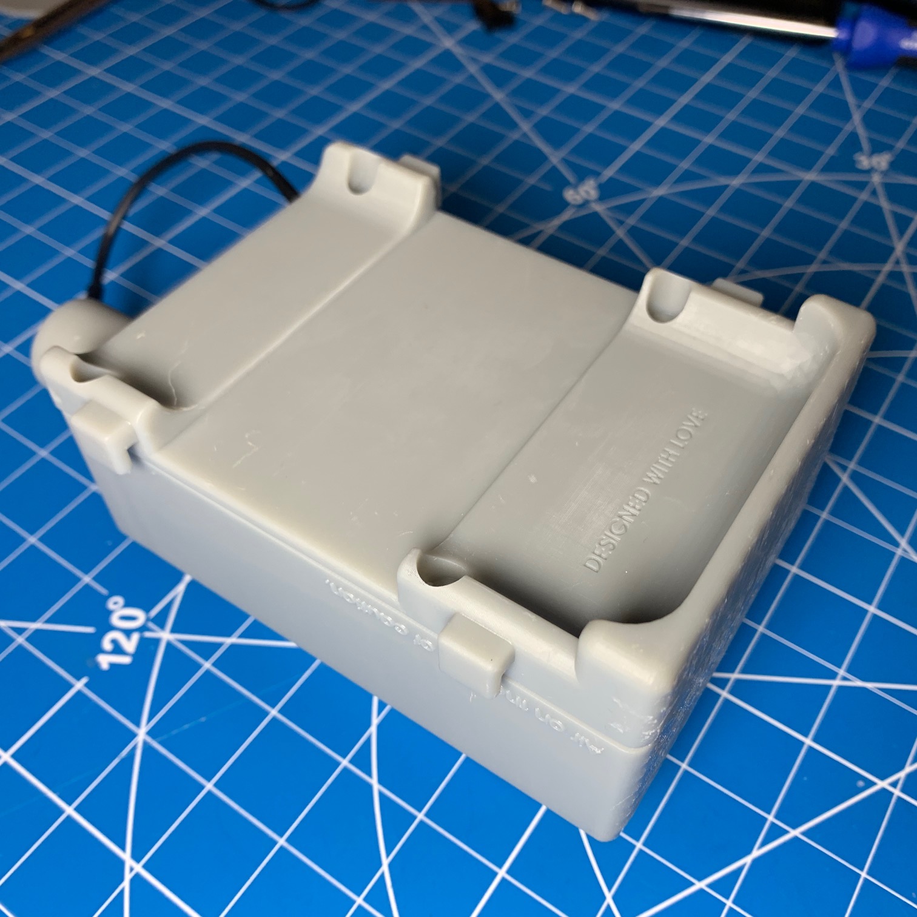
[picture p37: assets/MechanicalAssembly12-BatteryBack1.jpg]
Slide on the Battery Back
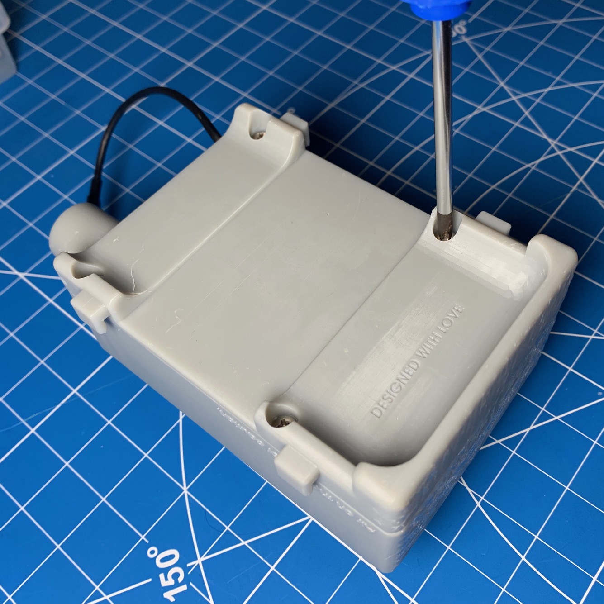
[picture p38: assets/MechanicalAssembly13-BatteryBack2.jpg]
Screw on the Battery Back
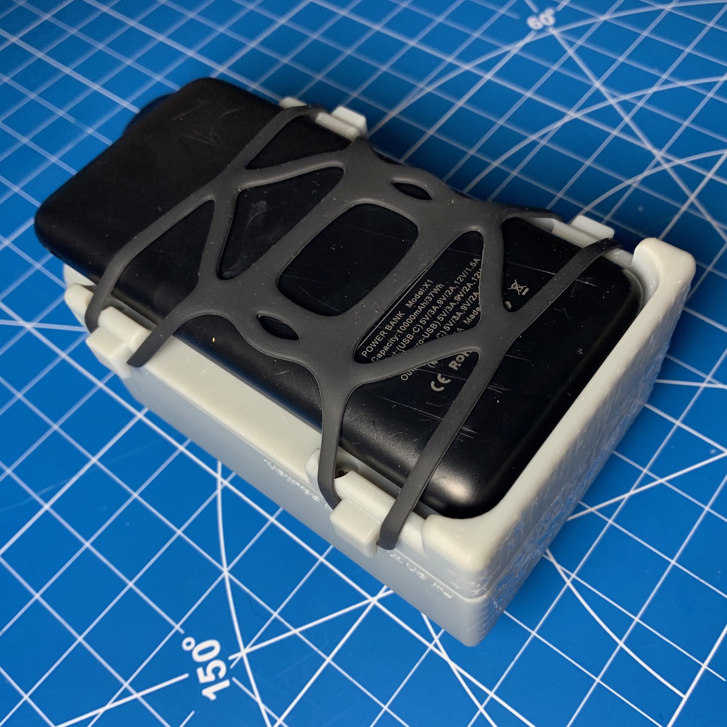
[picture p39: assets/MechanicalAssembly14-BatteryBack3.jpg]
Battery Install
|  |  |  |

**Step 9:** Take one of the filter gaskets and put it onto the inlet bayonet.

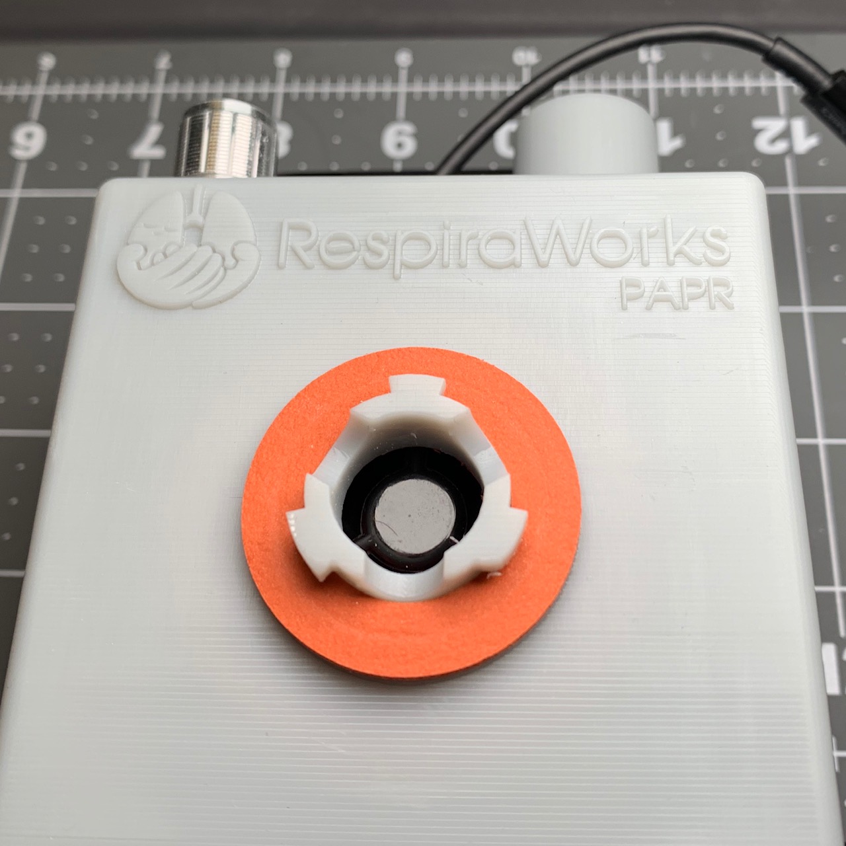
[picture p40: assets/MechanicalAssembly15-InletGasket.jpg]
Inlet Filter Gasket


**Step 10:** Install the shoulder strap.

|                            |                             |
|:--------------------------:|:---------------------------:|
| Install Shoulder straps | Install Shoulder Straps |

**Step 11:** Assembly Complete.  Plug in and test!  The blower should spin counter-clockwise.  After confirming proper operation, install the bayonet filter cartridge.  

Completed Assembly

|                            |                             |
|:--------------------------:|:---------------------------:|
Install Filter | Install Filter

----

## Mask Assembly Instructions

### 6100/6200/6300 Half Facepiece Mask

Note that 6100 is the small side, 6200 is medium, and 6300 is large.  These instructions and the 3D-printed pieces will work with all three sizes.

These modifications to the mask make it compatible with the PAPR, while also plugging the exhale valve and repurposing one of the inlet filters as an outlet filter.  This converts the mask into a full 2-way PAPR that filters both inhaled and exhaled air.

**Step 1:** Select one side of the mask to be the outlet filter side.  Remove the check valve membrane from the one-way valve on that side.  Install the bayonet filter cartridge onto that side.  On the opposite side, leave the valve membrane in place and install the 3D-Printed Bayonet Mask Adapter.

|                            |                             |                             |
|:--------------------------:|:---------------------------:|:---------------------------:|
| Remove Valve Membrane | Install Parts | Bayonet Inlet Adapter |

**Step 2:** Remove the outlet valve cover.  A flat bladed screwdriver will help.  Leave the outlet valve membrane in place.  

|                            |                             |
|:--------------------------:|:---------------------------:|
| Remove Outlet Cover | Leave Outlet Membrane in Place |

Put one of the 3M filter gaskets over the membrane, followed by the outlet plug.

|                            |                             |
|:--------------------------:|:---------------------------:|
| Place Gasket | Place Plug |

**Step 3:** Reinstall the outlet valve cover, making sure it snaps into place, and mark it as sealed.

|                            |                             |
|:--------------------------:|:---------------------------:|
| Reinstall Outlet Cover | Label Outlet |

Completed Mask

----

## Testing

The following procesures are inteneded to be used with a Portacount machine to test the efficacy of the PAPR, masks, and the filter cartridges it uses.  Beware of counterfeit filter cartridges!  

The Portacount (and similar devices) measures the concentration of particulates in an air stream by counting the number of particles per volume sampled.  It tests filters and mask fit by comparing the sample air inside a respirator to the outside ambient air.  The fit factor or protection factor is simply the number of particles counted in the ambient sample divided by the number of particles counted in the respirator sample, for the same volume.

A proper P100 filter should register a protection factor of 1000 or greater (> 99.9% of particles filtered).

A properly-fitting resipirator should at minimum deliver a fit factor / protection factor of 100.  Things like poor-fitting masks, loose masks, leaks in the hose or PAPR assembly, and poor-quality filter cratridges can all contribute to lower protection factors.

For reference, with the PAPR design described here, and a well-fitted 6200 mask modified per the instructions on this page, I have measured a protection factor of > 1100 consistently (as sampled inside the mask using the testing adapter below).  500 is generally considered the lower limit for a non-PAPR half-facepiece mask.

### To test the 6200-series masks

- Refer to the Portacount manual for proper set up and required calibration checks before use.
- Make sure a filter gasket has been placed on the 6200 Sampling adapter.
- Place the 6200 Sampling Adapter between the mask and the exhale filter cartridge (if you have performed the PAPR mods to this mask, this is on the side where the one-way valve membrane has been removed).
- Connect the Portacount sampling tube to the sample outlet on the 6200 Sampling Adapter.
- Run the Portacount Fit Test.
- If you are getting poor results, you may want to test your filter cartridges separately to determine if the filter or the PAPR or the mask is at fault.

|                            |                             |
|:--------------------------:|:---------------------------:|
| Mask Sampling Adapter | Portacount Hookup |

### To test the filter cartridges

- Refer to the Portacount manual for proper set up and required calibration checks before use.
- Make sure a filter gasket has been placed on the Bayonet Filter Tester.
- Connect the Portacount sampling tube to the sample outlet on the Bayonet Filter Tester.
- Run the Portacount Fit Test.

----

## Future Work

Instructions and 3D print files to modify more masks, hoods, and helmets for use with the PAPR.
Modified Masks

Instructions on how to modify the outlet valves to enable filtering of the exhaled air.
Outlet Sealed

Edwin in an M-206 Full Face Helmet

----

## Design Diary

18 July 2020 Update:

Front Exploded View

Back Exploded View

This one protects me

This one protects you

10 July 2020 Udpate:

Front Exploded View

Back Exploded View

3DprintParts

## Full Disclaimer

**Regulatory Notice**

This product has not been cleared for medical use by the U.S. Food and Drug Administration.  The product should only be used during the declared COVID-19 public health emergency if FDA cleared or approved products are unavailable.  This product has not been evaluated for the prevention of specific diseases or infections, the filtering of surgical smoke or plumes, the filtering of specific amounts of viruses or bacteria, or the killing or reduction of the amount of viruses, bacteria or fungi.  Not recommended for use in a surgical setting where exposure to liquid, bodily or other hazardous fluids may be expected or for use in a clinical setting where infection risk level through inhalation exposure is high.  Not recommended for use in the presence of a high intensity heat source or flammable gas.  This product is intended for use by a single user.

**Liability Notice**

By using this product, the end user assumes all risks associated with its use, including the voiding of manufacturers’ warranties of devices with which the product is used, and agrees to hold harmless and waive any claims against RespiraWorks, its officers, employees and agents, and other persons or companies which may have contributed to the design and specifications.  EXCEPT WHERE SPECIFICALLY PROHIBITED BY LAW, NO WARRANTIES OF ANY KIND ARE OFFERED FOR THE PRODUCT DESIGN AND SPECIFICATIONS, INCLUDING WARRANTIES OF NON-INFRINGEMENT AND FITNESS FOR A PARTICULAR PURPOSE.

**Intellectual Property License**

Individuals and organizations are free to use, copy, and share this design and specifications, including for commercial manufacture, without payment of any fees or charges, and for the duration of the declared COVID-19 public health emergency only, but may not assert ownership in the design and specifications.

**Notice to Manufacturers**

Individuals or organizations that manufacture products utilizing this design and specifications are responsible for any federal or state regulatory requirements that apply to the manufacture of products intended for medical use, and are responsible for informing health care providers to which the product is supplied that they are responsible for decisions regarding appropriate personal protective equipment for their personnel.  The distribution or sale of products manufactured using this design and specifications must include the Regulatory Notice and the Liability Notice as set forth above displayed prominently on packaging and marketing materials, as well as any information required by the FDA or other governmental authorities.

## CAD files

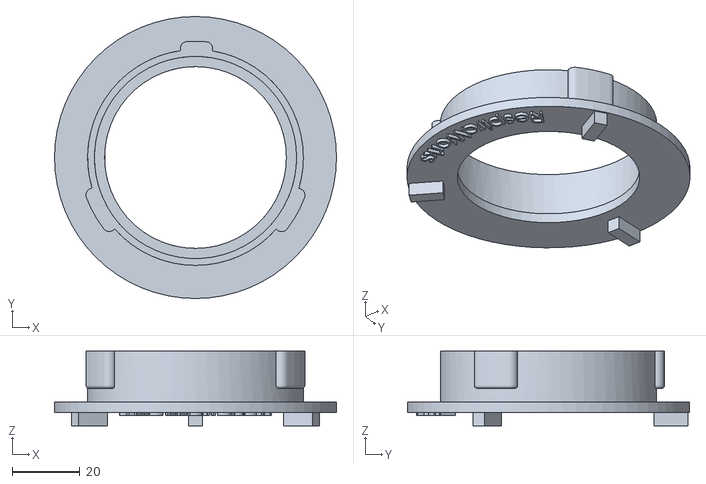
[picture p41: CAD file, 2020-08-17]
release-candidates/PAPRmasks/PAPRmasks-6700-FullFaceMaskPlate-V1.stl
83.0 x 83.0 x 22.0

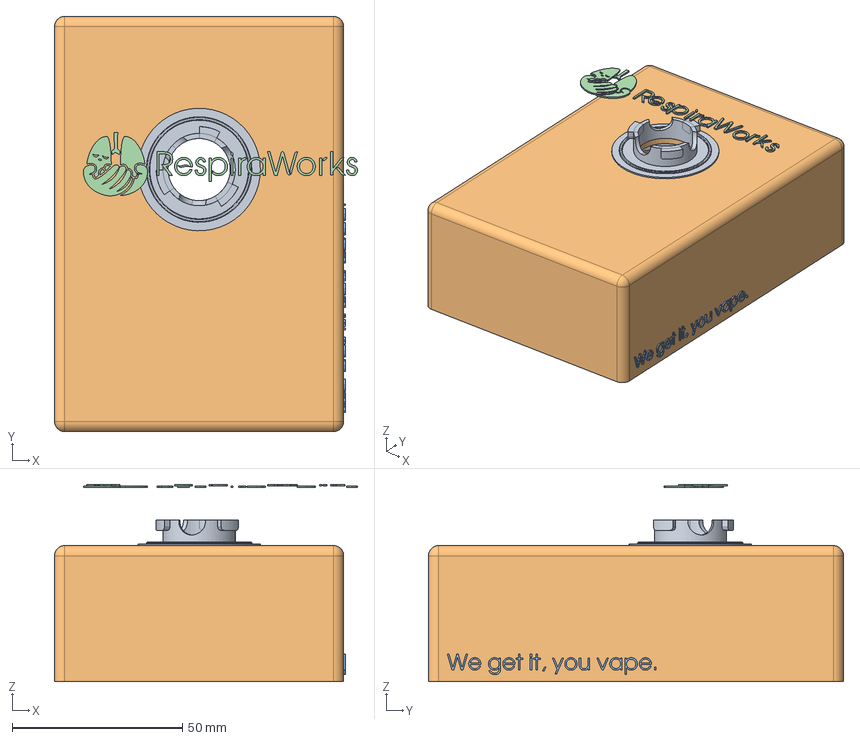
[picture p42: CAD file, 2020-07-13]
sandbox/PAPR-MAIN-V4.FCStd
89.0 x 122.0 x 58.0 mm
InletFilterBayonet
LidBlockBasic
VapeText
RW-LogoHorizontal-1mm-extrude001

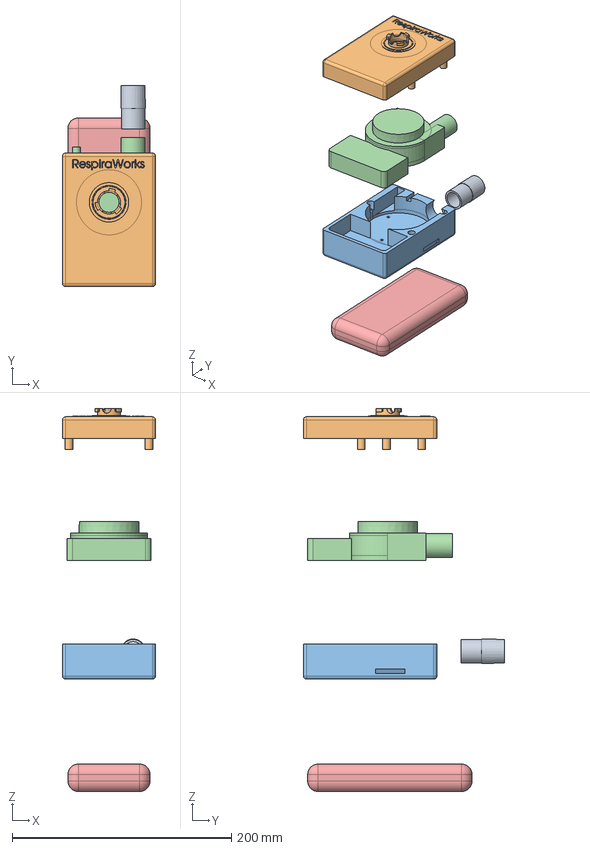
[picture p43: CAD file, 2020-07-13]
sandbox/PAPR-MAIN-V3-image.FCStd
85.0 x 183.8 x 349.5 mm
BlowerOutletAdapter-V3
PAPR-Lower-V3
PartsShow
BatteryPocket001

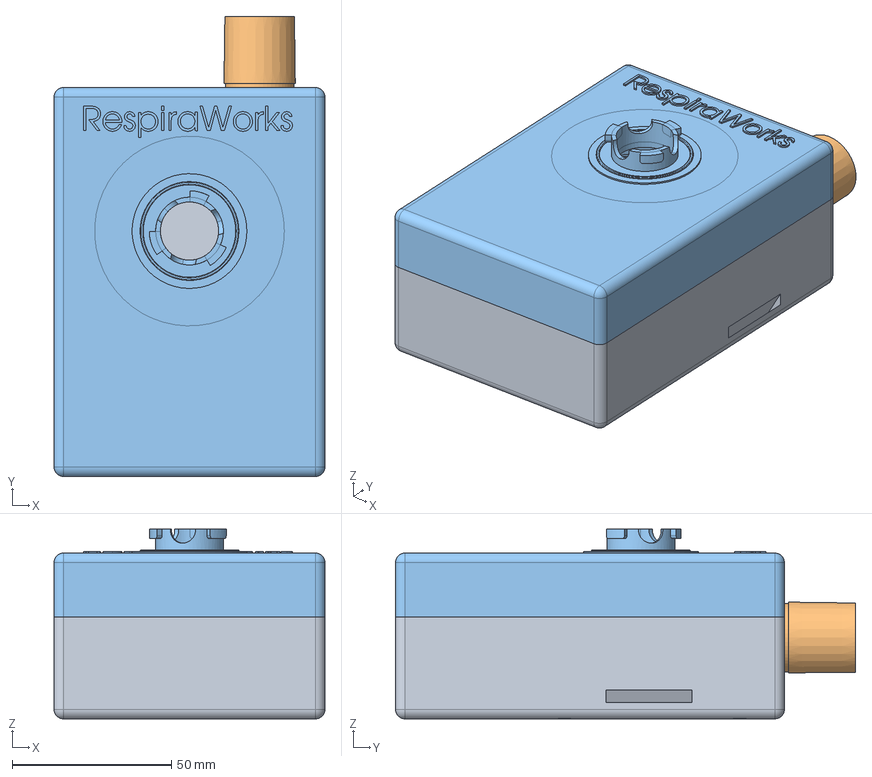
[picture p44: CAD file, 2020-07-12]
sandbox/PAPR-MAIN-V3.FCStd
85.0 x 144.3 x 59.5 mm
PAPR-Lower-V3
BlowerOutletAdapter-V3
Lid

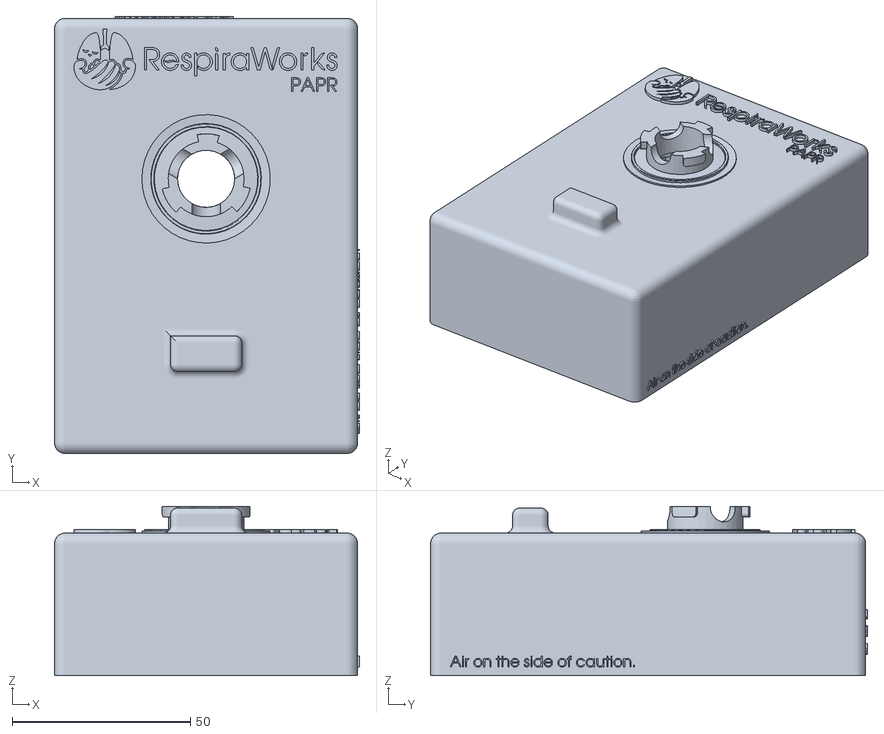
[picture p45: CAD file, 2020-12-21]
release-candidates/PAPR-Rev10/PAPRv10-Body.stl
85.5 x 122.5 x 47.5

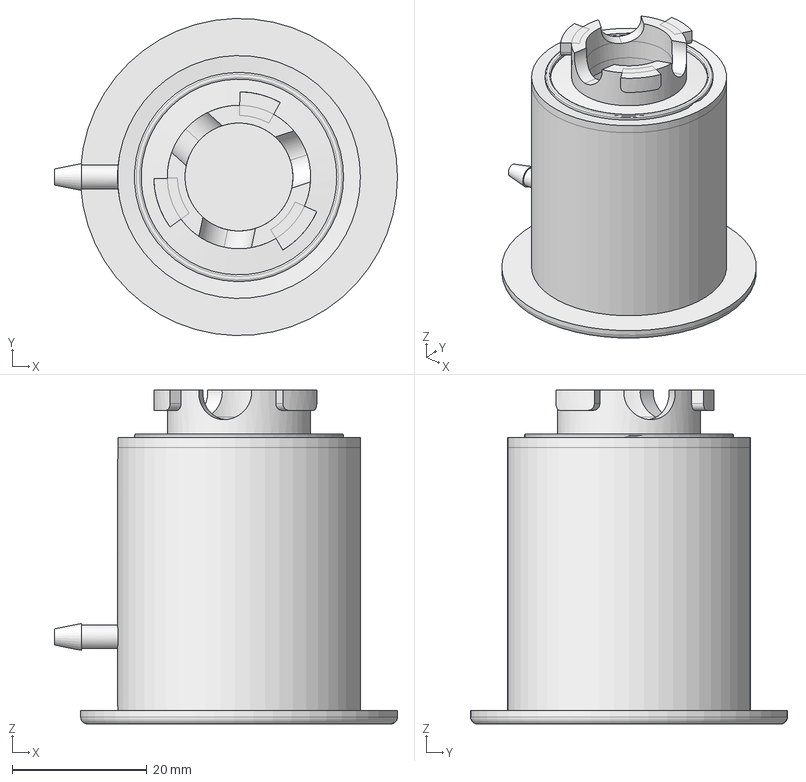
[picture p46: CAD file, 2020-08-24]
release-candidates/PAPRtest/PAPRtest-Portacount-BayonetFilterTester.FCStd
50.8 x 47.0 x 49.5 mm

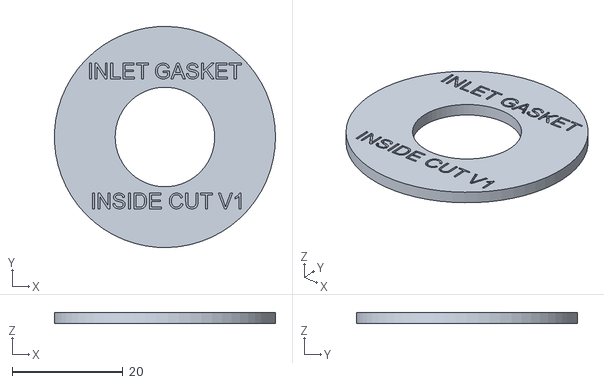
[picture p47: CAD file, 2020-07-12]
release-candidates/tools/InletGasketJigInsideV1.stl
40.0 x 40.0 x 2.00

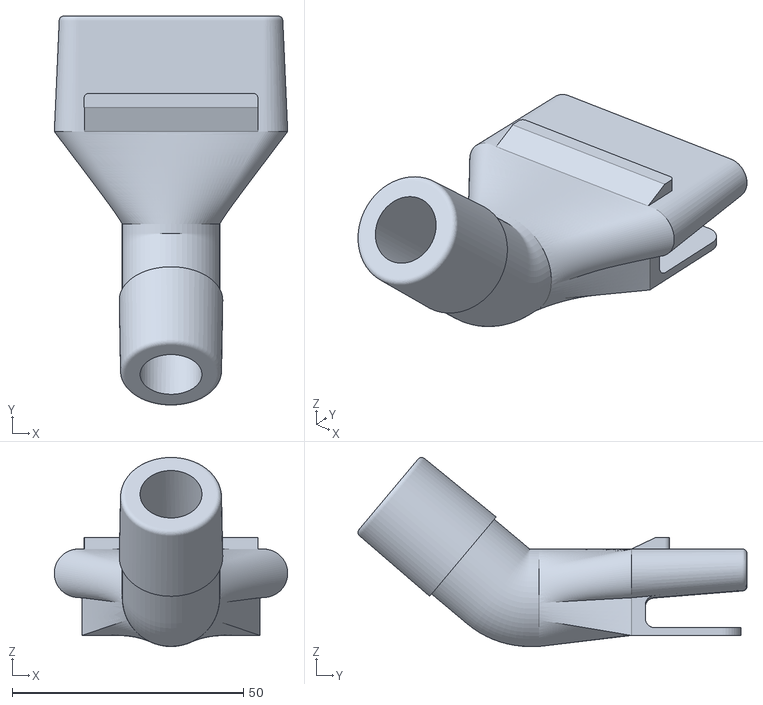
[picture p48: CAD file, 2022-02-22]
sandbox/PAPR-HF-800-Adapter-angled.stl
50.5 x 84.1 x 40.9

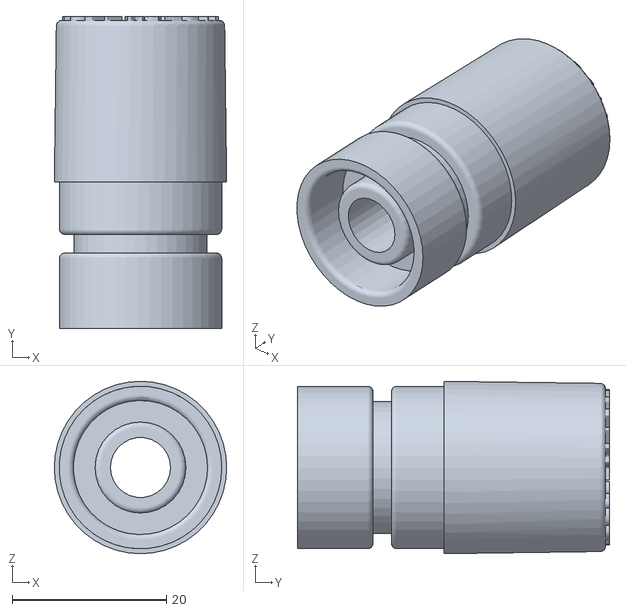
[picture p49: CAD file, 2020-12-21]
release-candidates/PAPR-Rev10/PAPRv10-OutletAdapter.stl
22.4 x 40.5 x 22.4

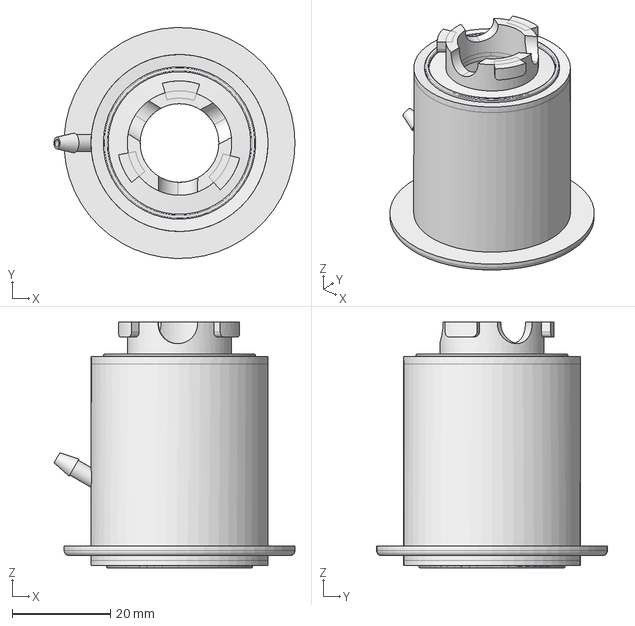
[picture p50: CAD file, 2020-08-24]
release-candidates/PAPRtest/PAPRtest-Portacount-6200SamplingAdapter.FCStd
49.0 x 47.0 x 50.0 mm

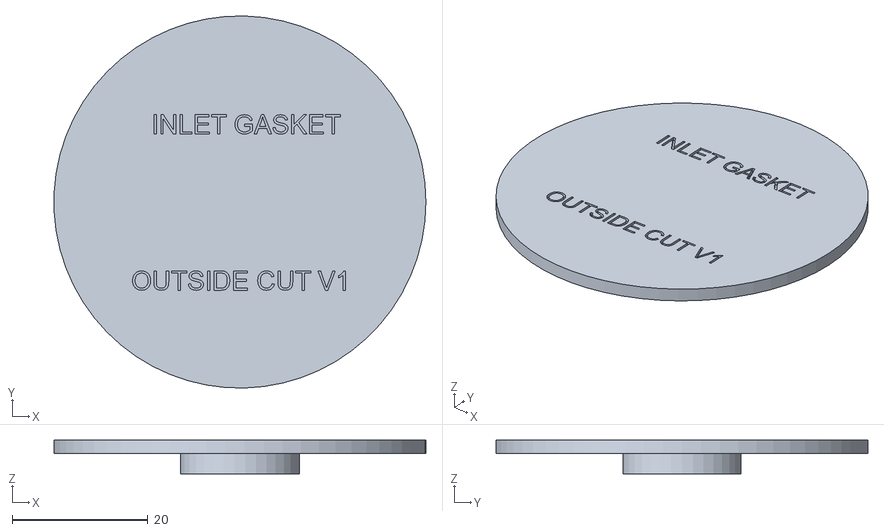
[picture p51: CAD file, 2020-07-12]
release-candidates/tools/InletGasketJigOutsideV1.stl
54.8 x 54.8 x 5.00

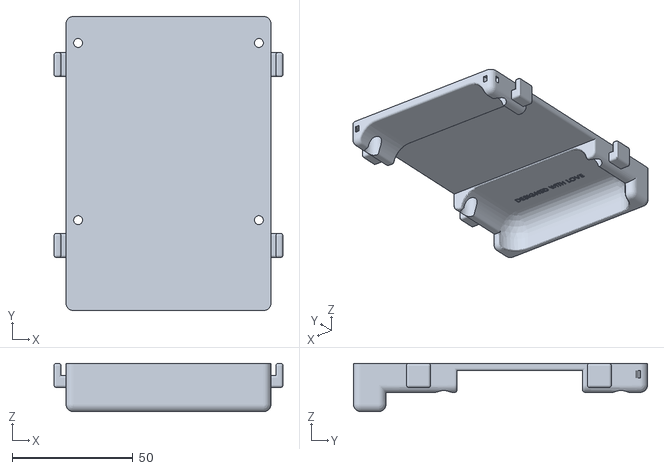
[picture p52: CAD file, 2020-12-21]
release-candidates/PAPR-Rev10/PAPRv10-BatteryBack.stl
95.0 x 122.0 x 20.0

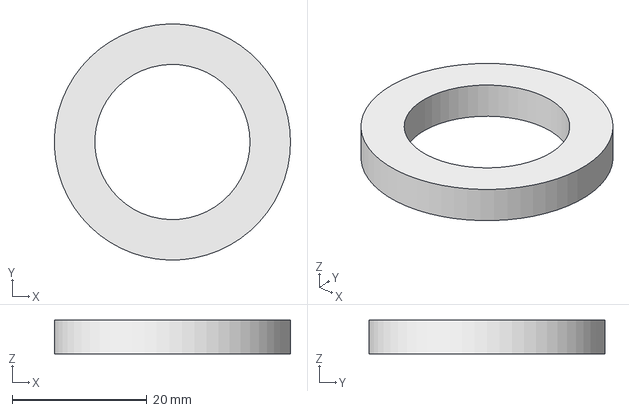
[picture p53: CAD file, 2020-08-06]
release-candidates/PAPRmasks/PAPRmasks-6200-OutletPlug-V1.FCStd
35.0 x 35.0 x 5.00 mm

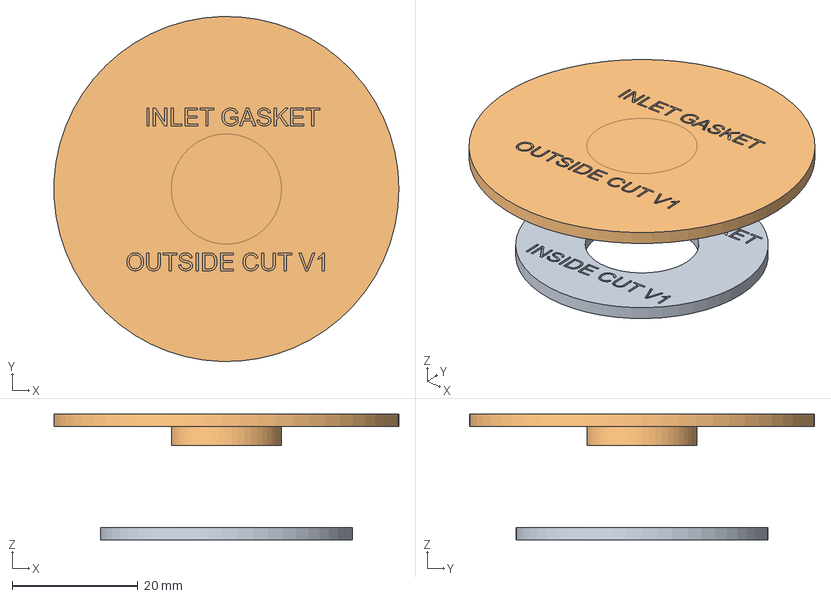
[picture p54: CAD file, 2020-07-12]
release-candidates/tools/InletGastketJigs.FCStd
54.8 x 54.8 x 20.0 mm
InletGasketJigInsideV1
InletGasketJigOutsideV1

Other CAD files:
release-candidates/PAPRmasks/PAPRmasks-6700-FullFaceMaskPlate.FCStd
sandbox/PAPRmasks-6700-FullFaceMaskPlate.FCStd
release-candidates/PAPR-Rev10/PAPRv10-OutletKey.stl
release-candidates/PAPR-Rev9/PAPR-BatteryBack-V9.stl
release-candidates/PAPR-Rev9/PAPR-Body-V9.stl
release-candidates/PAPR-Rev9/PAPR-OutletAdapter-V9.stl
release-candidates/PAPRmasks/PAPRmasks-6200-OutletPlug-V1.stl
release-candidates/PAPRmasks/PAPRmasks-BayonetInletAdapter-V1.FCStd
release-candidates/PAPRmasks/PAPRmasks-BayonetInletAdapter-V1.stl
release-candidates/PAPRtest/PAPRtest-Portacount-6200SamplingAdapter.stl
release-candidates/PAPRtest/PAPRtest-Portacount-BayonetFilterTester.stl
sandbox/3M-Bayonet-F-TestPrint-v7.stl
sandbox/3M-Bayonet-F-TestPrint.stl
sandbox/3M-Bayonet-F-test.stl
sandbox/BayonetBaseFemale.FCStd
sandbox/BayonetBaseFemale2.FCStd
sandbox/BayonetBaseFemaleV3.FCStd
sandbox/BayonetBaseFemaleV4.FCStd
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

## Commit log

2020-07-11 initial creation
    [3M-Bayonet-F-TestPrint-v7.stl, 3M-Bayonet-F-TestPrint.stl, 3M-Bayonet-F-test.stl, BayonetBaseFemale.FCStd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]
2020-07-11 adding tweaks
    [BayonetBaseMaleV3.FCStd, BayonetMtestV3.stl, BlowerInletAdapter-V2.FCStd, BlowerInletAdapter-V3.FCStd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]
2020-07-12 adding gasket jigs and new main 3D model with lid and inlet assembly
    [BlowerInletAdapter-V4.FCStd, BlowerInletAdapter-V4.stl, BlowerOutletAdapter-V3.FCStd, InletGasketJigInsideV1.stl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]
2020-07-12 fix inlet tab height, add logo
    [PAPR-MAIN-V3.FCStd]
2020-07-13 added logo V4 work in progress
    [PAPR-Lid-V3.stl, PAPR-MAIN-V3-image.FCStd, PAPR-MAIN-V4.FCStd, logo.FCStd]
2020-07-13 completed PAPR prototype v4
    [logo.FCStd]
2020-07-14 added V6 design: hollows out blower pocket more for easier assembly, change to threaded outlet adapter, updated mounting hole placements
    [InletGasketJigInsideV1.stl, InletGasketJigOutsideV1.stl, InletGastketJigs.FCStd, PAPR-BatteryBack-V4.stl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]
2020-07-17 created V8 with reinforced bayonet attachment and widened lock slot. WIP: refine lock slot, reduce step changes in the outlet adpater to reduce whistling, add text to unplug when not in use.
2020-07-18 added bayonet mask adapter. added V8 WIP: refined lock slot, removed step changes from output adapter, added unplug text. V8 todo: reduce size and strengthen battery velcro strap slot.
    [PAPR-MaskAdapter-V1.FCStd, PAPR-MaskAdapter-V2.FCStd, logo-V2.FCStd]
2020-07-19 updated readme with example filter and mask
2020-07-25 created PAPR V9 and created release candidate folder
    [InletGasketJigInsideV1.stl, InletGasketJigOutsideV1.stl, InletGastketJigs.FCStd, PAPR-6200MaskAdapter-V1.FCStd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]
2020-07-27 small adjustments to mounting points and outlet adapter chamfer
    [MadeByAdorableWeirdos.FCStd, PAPR-BatteryBack-RubberBand-V9.stl, PAPR-OutletAdapter-V9.stl]
2020-07-27 added outlet key removal feature
    [PAPR-Body-V9.stl, PAPR-OutletKey-V9.stl]
2020-07-29 updated with notch for removing outlet key, plus shortened outlet key for better fit. Added chin to battery back for stability
2020-08-04 printability tweaks, elastic mount battery back is now the standard design.
    [PAPR-BatteryBack-RubberBand-V9.stl, PAPR-BatteryBack-V9.stl, PAPR-Body-V9.stl, PAPR-OutletAdapter-V9.stl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]
2020-08-04 Update README.md
    updated BOM and provided a skeleton for assembly procedure
2020-08-06 added outlet plug and full face mask plate
    [PAPR-6200-OutletPlug-V1.FCStd, PAPR-6700-FullFaceMaskPlate.FCStd, RespiraWorksCircularText.FCStd]
2020-08-12 moved outlet position 0.5mm to aid assembly, updated full face mask plate for 2.3" window
    [PAPR-6700-FullFaceMaskPlate.FCStd, PAPR-Body-V9.stl]
2020-08-13 reverted 0.5mm outlet shift as this didn't actually improve ease of assembly, keeping the outlet adapter position shift
    [PAPR-Body-V9.stl, PAPR-OutletAdapter-V9.stl]
2020-08-17 Inceptionev/add assembly instructions (#1)
    * adding electrical and mechanical instructions
    * spelling and formatting
    * formatting
    * adding photos to assembly procedure
    * adding instruction photos and moving ready files to release-candidates. Reorganized separate folders for PAPR, masks, and tools
    * adding BOM items for mask mods and relinking 3d files to release-candidate
    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
    [InletGasketJigInsideV1.stl, InletGasketJigOutsideV1.stl, InletGastketJigs.FCStd, PAPR-6200-OutletPlug-V1.FCStd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]
2020-08-21 Add 3d printing instructions. This should make the Build Instructions feature-complete (#3)
    * adding instructions
    * formatting and specify softness for gasket
    * formatting fixes
    * mask asssembly instructions no longer work in progress.
2020-08-23 Gordonk/mght (#6)
    * Add files via upload
    Adding male garden hose thread (MGHT) outlet adapter STL and Solidworks files
    * Update README.md
    * moving commit changes over from master, moving added files inside sandbox folder
    * correction to sandbox link
    [PAPR-OutletAdapter-V9-with_MGHT.SLDPRT, PAPR-OutletAdapter-V9-with_MGHT.STL]
2020-08-24 Inceptionev/add testing adapters (#4)
    * initial creation
    * adding testing parts and ToC for the readme
    * added table of contents
    * added photos for mask testing
    * Revert "Update README.md"
    This reverts commit 2eeb5f17c23c10d9b323472d73ad1b0e3589d15a.
    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
    [InletGasketJigInsideV1.stl, InletGasketJigOutsideV1.stl, InletGastketJigs.FCStd, PAPRtest-Portacount-6200SamplingAdapter.FCStd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]
2020-09-01 print optimization: rounding corners and fit margins (#7)
    * print optimization: rounding corners to reduce print distortions. Fit margin added to potentiometer and lock slot pockets.
    * added tips for chasing the threads in the body
    * updating freecad source file
    * updated per review notes
    [PAPR-Body-V9.stl]
2020-10-02 adding M200 versaflo helmet adapter, work in progress. Body fits but retaining ring needs some work.
    [PAPR-M200-HelmetAdapter.FCStd]
2020-10-26 added material tester
    [PAPRtools-PortacountMaterialTestAdapter.FCStd]
2020-11-25 Inceptionev/add photo and cards (#18)
    * adding files for PAPR info cards and changing readme intro image to reflect that the PAPR is wearable
    * update readme
    * updating to fix pdf link and reflect 20hr battery runtime
    * fix image scaling
    * fix image scaling
    * clarify PDF link
    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
2020-12-21 PAPRv10 adds waistband option and improves screw locations to fix gapping issue (#22)
    * creating PAPRv10
    * rename file
    * adding STL files
    * adding printing project files
    * Shifted hole positions for better strength
    * improved battery back for waist mounting
    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
    [PAPRv10-BatteryBack.stl, PAPRv10-Body.stl, PAPRv10-OutletAdapter.stl, PAPRv10-OutletKey.stl]
2022-02-22 adding prototype HF-800 Adapter
    [PAPR-HF-800-Adapter-angled.ipt, PAPR-HF-800-Adapter-angled.stl]
